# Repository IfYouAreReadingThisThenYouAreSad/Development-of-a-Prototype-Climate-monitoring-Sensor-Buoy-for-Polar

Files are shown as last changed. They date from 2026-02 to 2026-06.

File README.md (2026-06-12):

# Development of a Prototype Climate-Monitoring Sensor Buoy for Polar Regions

---

# 1.0 About

This project aims to develop a prototype of a mass-deployable climate-monitoring buoy optimised for polar regions. The system autonomously measures and communicates key environmental parameters such as sea ice thickness, temperature, salinity, and local imagery. It is intended for deployment in both ice and open water, operating with minimal energy and maintenance.

Project Demo (https://www.youtube.com/watch?v=G8KJ4cSrFfc)

---

# 2.0 Sensors

The buoy contains sensors that help measure essential climate variables and the overall health of the buoy. Sensors include:

- Sea ice thickness (EMI)
- Turbidity
- Salinity (and possible antifouling monitoring)
- UV and ambient light exposure
- Temperature (external)
- Temperature (internal)
- Tilt (compensates for angle for the sea ice measurement system)
- IMU (wave spectrum)
- GPS
- Bluetooth (for the prototype only, will be replaced by satellite communication)
- Battery monitoring
- SD card (onboard storage)
- Camera (with onboard image processing)

The image below shows the buoy's sensors and their locations.

<p align="center">
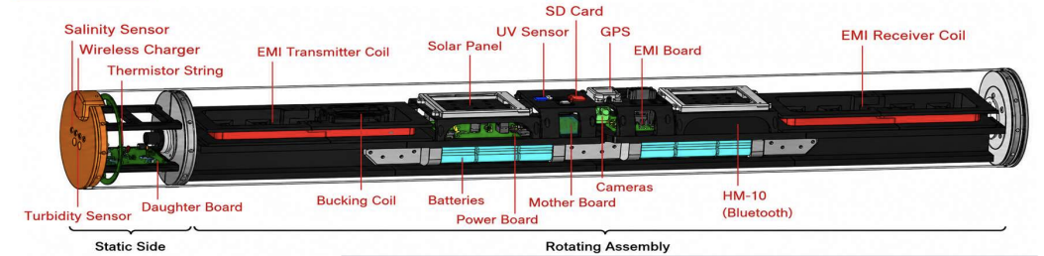
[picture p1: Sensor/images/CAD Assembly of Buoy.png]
Figure 1 shows CAD View of Buoy
  
</p>
<p align="center">Figure 1: CAD view of the buoy</p>

---

# 3.0 Mechanical Design

The buoy has a rotating side and a static side. The static side contains sensors such as turbidity and salinity, the external temperature sensors, and the IMU. These need to stay fixed, and this side is weighted slightly so that, in water, they can work effectively without being affected by the rotating part of the system.

The buoy has a rotating side, where a rotating I-beam is used to ensure proper orientation of the buoy. Due to the buoy being mass-deployed and dropped anywhere in the Arctic, this allows the system to always align orientation-sensitive sensors, such as the EMI sensor, which must always be horizontal to the sea ice. It also keeps the GPS, UV sensor, and Bluetooth module pointing towards the sky, and the camera pointing perpendicular to the ice for the best view.

For both sides to work, two PCBs (shown below) were made, connected through a slip ring. The daughter board digitises the data on the static side and adds a checksum. The mother PCB then reads this data and sends it via satellite. This is a very brief explanation — for more detail, please read the attached report in this repository.

<p align="center">
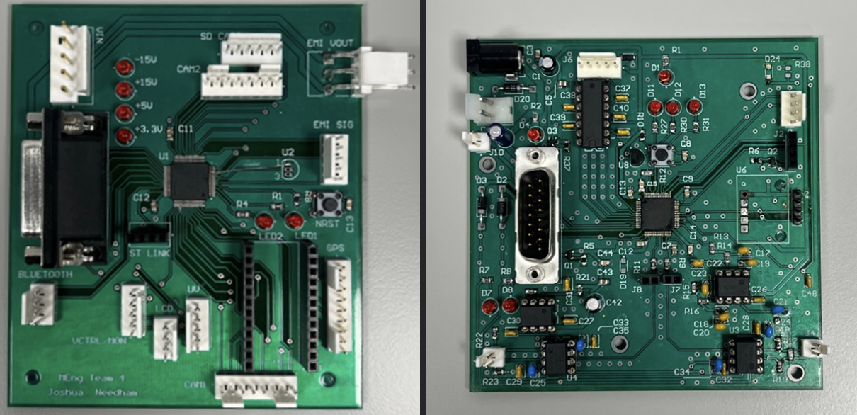
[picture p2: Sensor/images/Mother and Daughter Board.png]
Figure 2 shows the Mother and Daughter board
  
</p>
<p align="center">Figure 2: Mother and daughter boards</p>

---

# 4.0 GUI

A GUI was designed to interact with the system. This allows for monitoring of the buoy and for manual requests of data. In this prototype, data must be requested manually, but in the real system data will be sent periodically, with the frequency changing depending on whether the buoy is on ice, in water, or on land. The GUI in the real design will still allow specific data to be requested, but will also allow monitoring of the health, position, and data of multiple buoys. An image of the GUI is shown below.

<p align="center">
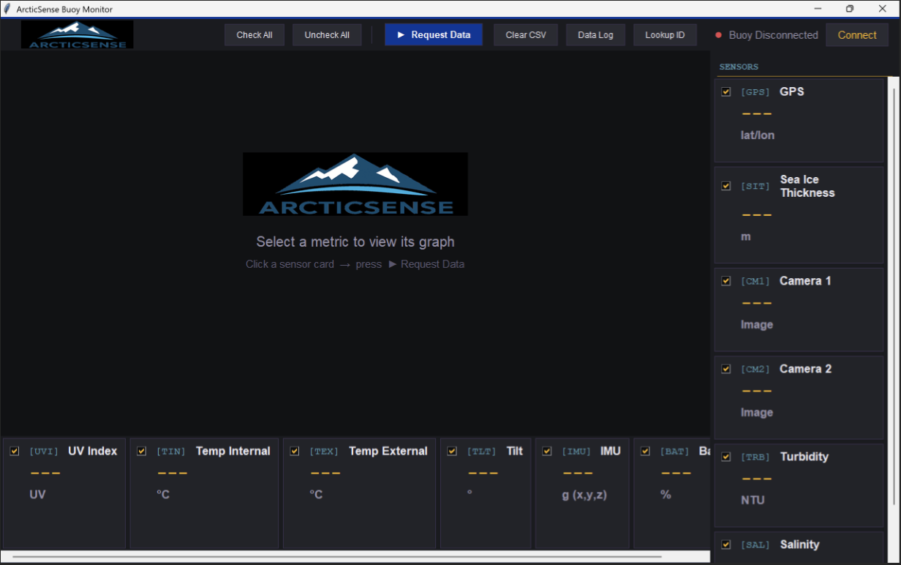
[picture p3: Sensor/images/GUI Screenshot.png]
Figure 3 shows GUI Interface
  
</p>
<p align="center">Figure 3: GUI interface</p>

---

# 5.0 System Architecture

<p align="center">
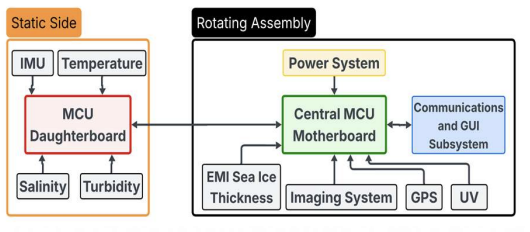
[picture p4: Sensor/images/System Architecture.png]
Figure 4 shows simplified System Architecture of Buoy
  
</p>
<p align="center">Figure 4: Simplified system architecture of the buoy</p>

---

# 6.0 Repository Structure

This repository is organised into folders, each corresponding to a specific sensor, hardware module, or subsystem. Code for each module was developed, compiled, and tested independently within its respective folder. Once verified, each module's code is integrated into a single project that combines all sensors, hardware, and subsystems into a fully functioning system.

This structure is designed to make it easier for external users to:

- Understand how each module works individually
- Navigate to specific hardware or sensor code
- Contribute to or modify individual subsystems without affecting the rest of the project

## Folder Overview

| Folder | Contents |
|--------|----------|
| `README` | This top-level overview of the project. |
| `Intergration` | The integrated mother and daughter board projects (`main.c` for each), the GUI application, and their associated READMEs. |
| `Sensors` | One folder per sensor/module, each containing its driver library and a README explaining its hardware, API, and usage. |
| `Report and Other Information` | The full project report and the project poster. |
| `PCB` | PCB design files for the mother and daughter boards. This may be sent separately if it isn't ready in time for handover. |

---

# 7.0 More Information

Each README in this repository is intentionally short, providing baseline information on the hardware and how to use the code associated with each sensor or section. For more information, calibration data, and results, please read the report attached in this repository.

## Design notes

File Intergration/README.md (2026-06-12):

# ArcticSense

A prototype autonomous climate-monitoring sensor buoy designed for polar deployment. The system collects Essential Climate Variables such as sea ice thickness, ocean temperature, turbidity, salinity, and UV radiation, then transmits them remotely to a ground-station GUI.

Developed as a final-year engineering project in partnership with the **British Antarctic Survey**.

---

## System Overview

```
Ground Station (Python GUI)
        │
        │  Bluetooth Low Energy (HM-10)
        │  [target: Iridium 9603N satellite modem]
        ▼
┌─────────────────────────────────────┐
│        Motherboard  (STM32F405RGT6) │
│  UV · GPS · Tilt · Battery          │
│  EMI · Cameras · Temp · Humidity    │
│                      UART ↕         │
│      Daughterboard  (STM32F405RGT6) │
│  Thermistors · Turbidity · Salinity │
│  Temp · Humidity· IMU               │
└─────────────────────────────────────┘
```

The **Motherboard (MB)** receives commands from the GUI, forwards the request to the **Daughterboard (DB)**, reads its own sensors, assembles the combined payload, and returns it to the GUI as 20-byte fragments. The DB is a silent slave, it never initiates communication.

The **HM-10 BLE module** is a development stand-in for the target **Iridium 9603N** satellite modem. The 20-byte fragment size and 5-byte command frame were chosen to fit within the Iridium SBD 340-byte message limit, so migrating to satellite requires only a transport-layer swap.

---

## Quick Start

To run the ground station on a laptop with BLE:

```bash
cd GUIV3
pip3 install bleak Pillow tkintermapview matplotlib
python3 run.py
```

See [`GUI/README.md`](GUI/README.md) for full setup instructions, file layout, and GUI feature reference.

To flash firmware, open either the `Motherboard/` or `Daughterboard/` project in **STM32CubeIDE** and flash via ST-Link.

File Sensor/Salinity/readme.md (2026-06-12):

# Salinity (STM32)

---

# 1. Overview

A custom made salinity sensor was made for the buoy to save money and to help expand the functionality of traditional salinity sensors. A 4-probe salinity sensor was used, which leads to better long-term measurements than a traditional 2-probe sensor. The sensor calculates salinity through the cell constant, which was found through calibration (read the final report for more information). Additionally, the salinity sensor has also been calibrated for some temperature change, but more work needs to be done on this.

---

# 2. Hardware

The sensor uses the daughter board's DAC. This is run through a low-pass filter, or can be jumped with a 0Ω resistor so it acts as a unity gain amplifier. Next, the signal goes through an AC coupling stage to remove any DC components from the DAC. It is then passed through a shunt resistor before going to the outer electrodes. The voltage across the shunt goes through an instrumentation amplifier, which adds gain and shifts it up to 1.65V to use the ADC's full range. The inner electrodes go through a duplicate instrumentation amplifier arrangement. All of this is shown in the image below.

<p align="center">
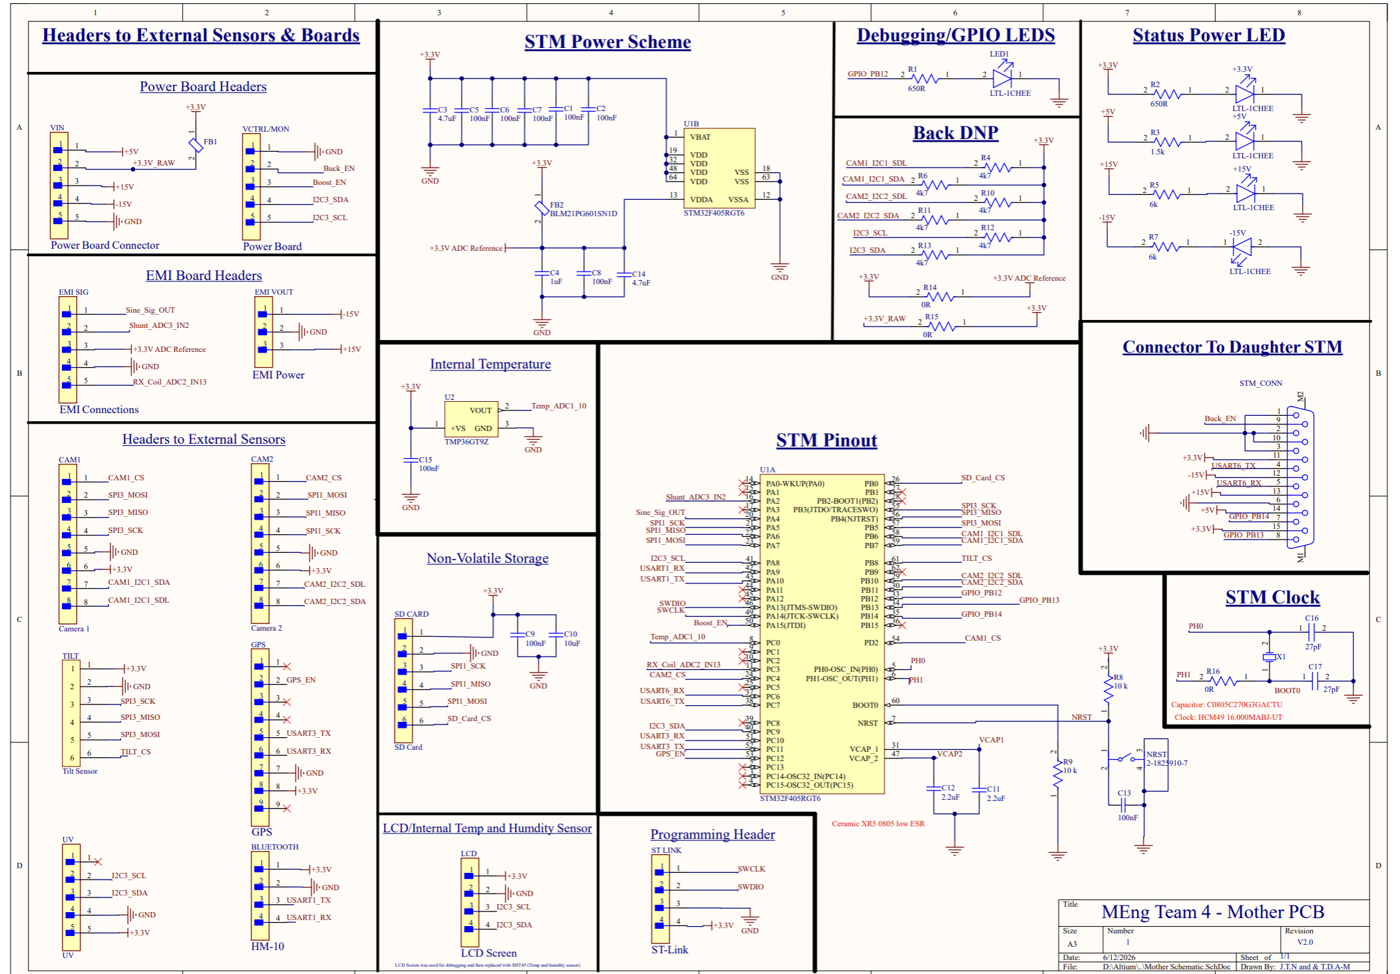
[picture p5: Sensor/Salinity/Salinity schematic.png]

</p>

<p align="center"><b>Figure 1:</b> Salinity sensor signal chain — DAC excitation, AC coupling, shunt, and instrumentation amplifier stages.</p>

---

# 3. Hardware Connections

The salinity sensor is driven and read via the **STM32 DAC and ADC** peripherals, not I2C.

## STM32 ↔ Salinity Circuit Connections

| Signal | STM32 / System | Description                                      |
|--------|-----------------|---------------------------------------------------|
| DAC_OUT2 | DAC Channel 2 | 7 Hz sine excitation signal, sent to outer electrodes via shunt |
| ADC1_IN9 | ADC1 (master) | Current channel (shunt voltage), DMA captured     |
| ADC2_IN14 | ADC2 (slave)  | Voltage channel (inner electrode voltage), DMA captured |
| TIM6    | Timer          | Triggers the DAC sine output (448 Hz update rate, 64-point LUT) |
| TIM3    | Timer          | Triggers simultaneous dual ADC1/ADC2 sampling     |

---

# 4. API

This module is implemented directly in `main.c` rather than as a separate driver library, as only one measurement function is required.

## Public Functions

| Function | Description |
|----------|-------------|
| `ConductivityResult Conductivity_Measure(void)` | Runs a full conductivity/salinity measurement cycle: safety check, DAC excitation, dual-ADC DMA capture, and conversion to conductivity and salinity. Always check `.status` before using the returned values. |

---

## Important `#define` Constants

| Variable | Description |
|----------|-------------|
| `SINE_SAMPLES` | Number of points in the DAC sine LUT (64). |
| `SINE_FREQ_HZ` | Excitation frequency (7 Hz). |
| `DAC_MID_COUNT` / `DAC_AMP_COUNT` | DAC LUT mid-rail and amplitude counts, set for a 1Vpp sine centred at 1.65V on a 3.3V/12-bit DAC. |
| `CYCLES_TO_CAPTURE` | Number of excitation cycles captured per measurement (16). |
| `ADC_BUF_SIZE` | Total dual-word ADC samples captured per measurement (`CYCLES_TO_CAPTURE * SINE_SAMPLES` = 1024). |
| `VREF` / `ADC_FULL_SCALE` | ADC reference voltage (3.3V) and full-scale count (4095) used to convert raw counts to volts. |
| `ADC_SAFETY_THRESHOLD` | Raw ADC count (~3.22V) above which a probe is considered shorted before excitation starts. |
| `CONDUCTIVITY_SCALE` | Cell constant used to convert the current/voltage RMS ratio to conductivity (mS), found through calibration. |
| `SALINITY_SCALE` | Constant used to convert conductivity (mS) to salinity (g/L). |

---

## Enums and Structs

### `ConductivityStatus`

Returned by `Conductivity_Measure()` for error handling.

| Value | Description |
|-------|-------------|
| `COND_OK` | Measurement completed successfully. |
| `COND_FAULT_SHORT` | ADC read close to 3.3V before excitation started, or the voltage channel read near zero — indicates a short or open circuit on the probes. |
| `COND_FAULT_TIMEOUT` | DMA capture did not complete within the 3 second timeout. |

### `ConductivityResult`

Struct returned by `Conductivity_Measure()`.

| Member | Description |
|--------|-------------|
| `ConductivityStatus status` | Result status — must be checked before using the other fields. |
| `float adc1_rms_V` | AC-RMS voltage measured on ADC1 (current/shunt channel). |
| `float adc2_rms_V` | AC-RMS voltage measured on ADC2 (voltage channel). |
| `float conductivity_mS` | Calculated conductivity in mS. |
| `float salinity_gL` | Calculated salinity in g/L. |

---

# 5. Code Flow

## Processing Steps

1. **Safety check**
   - Performs one poll-mode ADC conversion on each channel before any excitation is applied
   - If either ADC reads above `ADC_SAFETY_THRESHOLD` (~3.22V), the probes are assumed shorted and the measurement aborts with `COND_FAULT_SHORT`
   - Re-initialises ADC1 and ADC2 back into their DMA-triggered configuration afterwards

2. **Excitation**
   - Builds a 64-point sine LUT for a 1Vpp, 1.65V-centred signal
   - Starts the DAC on Channel 2 via DMA, driven by TIM6 to produce a 7 Hz sine wave
   - Waits ~50 ms (half a cycle) for the signal to settle

3. **Capture**
   - Starts simultaneous dual-ADC DMA capture (ADC1 master / ADC2 slave), triggered by TIM3
   - Captures 1024 dual-word samples (16 full excitation cycles)
   - Waits for DMA completion, with a 3 second timeout (`COND_FAULT_TIMEOUT` if exceeded)

4. **Shutdown**
   - Stops TIM3, ADC DMA, TIM6, and the DAC in sequence
   - Parks the DAC output at mid-rail (1.65V) briefly before stopping it, to avoid a floating-output glitch

5. **Conversion**
   - Computes the AC-RMS voltage of each channel (DC bias removed via a two-pass mean/variance calculation)
   - If the voltage channel RMS is near zero, returns `COND_FAULT_SHORT` (likely open circuit)
   - Calculates conductivity: `conductivity_mS = (I_rms / V_rms) * CONDUCTIVITY_SCALE`
   - Calculates salinity: `salinity_gL = conductivity_mS * SALINITY_SCALE`

---

# 6. Dependencies

- STM32 HAL Library
- STM32 ADC1 and ADC2 Peripherals (dual-simultaneous DMA mode)
- STM32 DAC Peripheral (Channel 2, DMA mode)
- TIM6 (DAC trigger) and TIM3 (ADC trigger)
- `math.h` (for sine LUT generation)

---

# 7. Example Usage (C)

```c
ConductivityResult result = Conductivity_Measure();

if (result.status == COND_OK)
{
    float conductivity = result.conductivity_mS;
    float salinity     = result.salinity_gL;

    BSP_LED_Toggle(LED_GREEN);
}
else if (result.status == COND_FAULT_SHORT)
{
    // Probe short or open circuit detected
    Error_Handler();
}
else
{
    // ADC DMA timeout — check TIM3 and DMA configuration
    Error_Handler();
}
```

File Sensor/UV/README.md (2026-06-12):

# UV Module (STM32)

If you are looking for libraries for **Arduino or Raspberry Pi** and information on the **LTR390-UV Ultraviolet Sensor**, please refer to the official Waveshare Wiki documentation:

https://www.waveshare.com/wiki/UV_Sensor_(C)

---

# 1. Overview

This directory contains a driver for interfacing with the **Digital LTR390-UV Ultraviolet Sensor** over I2C using an STM32 microcontroller.

The LTR390 enables real-time measurement of:
- Ambient light using the onboard ambient light sensor (ALS)
- Ultraviolet light

This module is used on the buoy to monitor UV light across seasons to help monitor climate change.

---

# 2. Hardware

The system uses the:

**Digital LTR390-UV Ultraviolet Sensor**

### Product Link
https://thepihut.com/products/digital-ltr390-uv-ultraviolet-sensor

<p align="center">
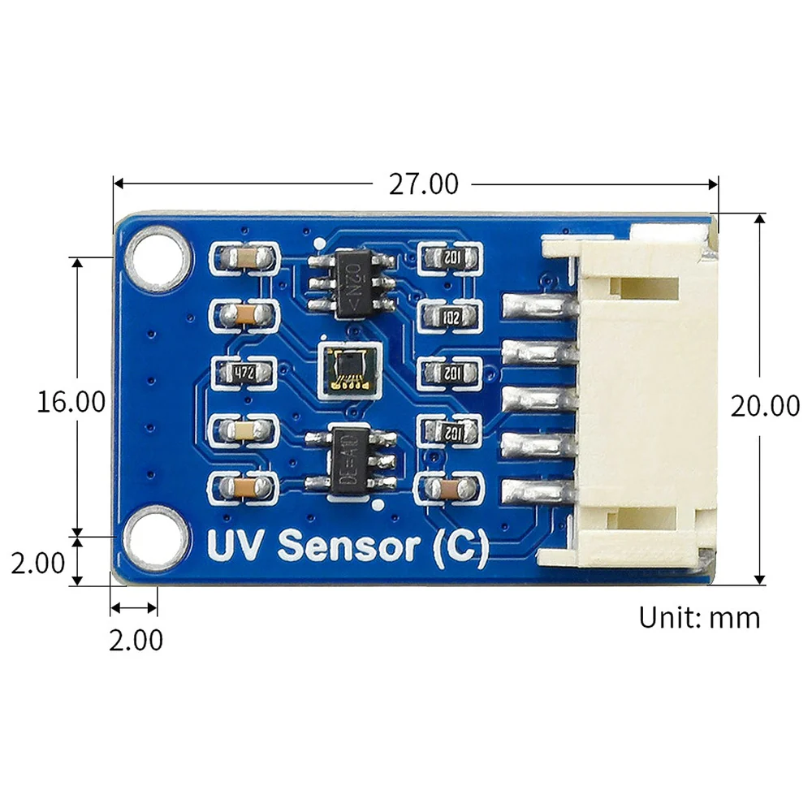
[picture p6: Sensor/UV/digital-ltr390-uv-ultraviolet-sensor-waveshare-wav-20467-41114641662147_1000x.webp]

</p>

<p align="center"><b>Figure 1:</b> UV Sensor Module</p>

---

# 3. Hardware Connections

The LTR390 communicates via the **I2C interface**.

## STM32 ↔ LTR390 Connections

| LTR390 Pin | STM32 / System | Description       |
|------------|----------------|-------------------|
| VCC        | 3.3V / 5V      | Module power      |
| GND        | GND            | Common ground     |
| SCL        | I2C_SCL        | I2C clock line    |
| SDA        | I2C_SDA        | I2C data line     |

---

## Example STM32F401 Pin Mapping

| STM32 Pin | Peripheral | Function  |
|-----------|------------|-----------|
| PB6       | I2C1_SCL   | I2C clock |
| PB7       | I2C1_SDA   | I2C data  |

---

# 4. API

## Constructor

| Function | Description |
|----------|-------------|
| `Ltr390Driver(I2C_HandleTypeDef *hi2c_)` | Initialises the driver with the STM32 I2C peripheral. Internal variables are reset during construction. |

---

## Important `constexpr` Class Variables

These variables are held constant at compile time and are currently set for this project's application. It may be worth reviewing these before compiling for a different project.

These constants are private members of the class in the `.hpp` file and are intentionally hidden from the user to prevent accidental modification.

| Variable | Description |
|----------|-------------|
| `WINDOW_FACTOR` | Compensates for UV loss through the buoy enclosure window. Set to 1.0 until the window material has been calibrated. |
| `DATA_READY_TIMEOUT_MS` | Maximum time the driver waits for the sensor to be ready before returning a `TIMEOUT` error. Used in `wait_data_ready()`. |
| `MEAS_RATE_DEFAULT` | Controls resolution and measurement rate. Bits [6:4] set resolution, bits [2:0] set rate. `ALS_INTEGRATION_TIME` updates automatically when this changes. |
| `GAIN` | Sets the photodiode gain. `ALS_GAIN` updates automatically when this changes. |
| `COUNTS_PER_UVI` | Reference sensitivity constant used to convert raw UV counts to UV Index. Must be recalculated from the datasheet if `GAIN` or `MEAS_RATE_DEFAULT` are changed. |

---

## Public Functions

| Function | Description |
|----------|-------------|
| `Ltr390Status init()` | Initialises the sensor by probing the I2C bus, setting resolution, sampling rate, and gain, then enabling the sensor in UV mode. |
| `Ltr390Status calculate_uv_index()` | Reads the UV sensor and calculates the UV Index. Result is stored internally and retrieved with `get_uv_index()`. |
| `Ltr390Status calculate_lux()` | Reads the ambient light sensor and calculates lux. Result is stored internally and retrieved with `get_lux()`. |
| `float get_uv_index()` | Returns the last UV Index value computed by `calculate_uv_index()`. |
| `float get_lux()` | Returns the last lux value computed by `calculate_lux()`. |

---

# 5. Enums

## `Ltr390Status`

Returned by all driver functions for error handling and debugging.

| Value | Description |
|-------|-------------|
| `Ltr390Status::OK` | Operation successful. |
| `Ltr390Status::I2C_NO_ACKNOWLEDGMENT` | Sensor did not ACK — check wiring, power, and I2C address. |
| `Ltr390Status::I2C_TRANSMIT_ERROR` | I2C failure when transmitting to the sensor. |
| `Ltr390Status::I2C_RECEIVE_ERROR` | I2C failure when receiving data from the sensor. |
| `Ltr390Status::TIMEOUT` | Sensor did not signal data ready within `DATA_READY_TIMEOUT_MS`. |
| `Ltr390Status::INVALID_ARGUMENT` | Invalid `WINDOW_FACTOR` value (must be greater than 0). |
| `Ltr390Status::RESOLUTION_SETUP_ERROR` | I2C error when writing the resolution / measurement rate register. |
| `Ltr390Status::GAIN_SETUP_ERROR` | I2C error when writing the gain register. |
| `Ltr390Status::UV_MODE_SWITCH_ERROR` | Failed to switch the sensor to UV measurement mode. |
| `Ltr390Status::ALS_MODE_SWITCH_ERROR` | Failed to switch the sensor to ambient light measurement mode. |

---

# 6. Code Flow

<p align="center">
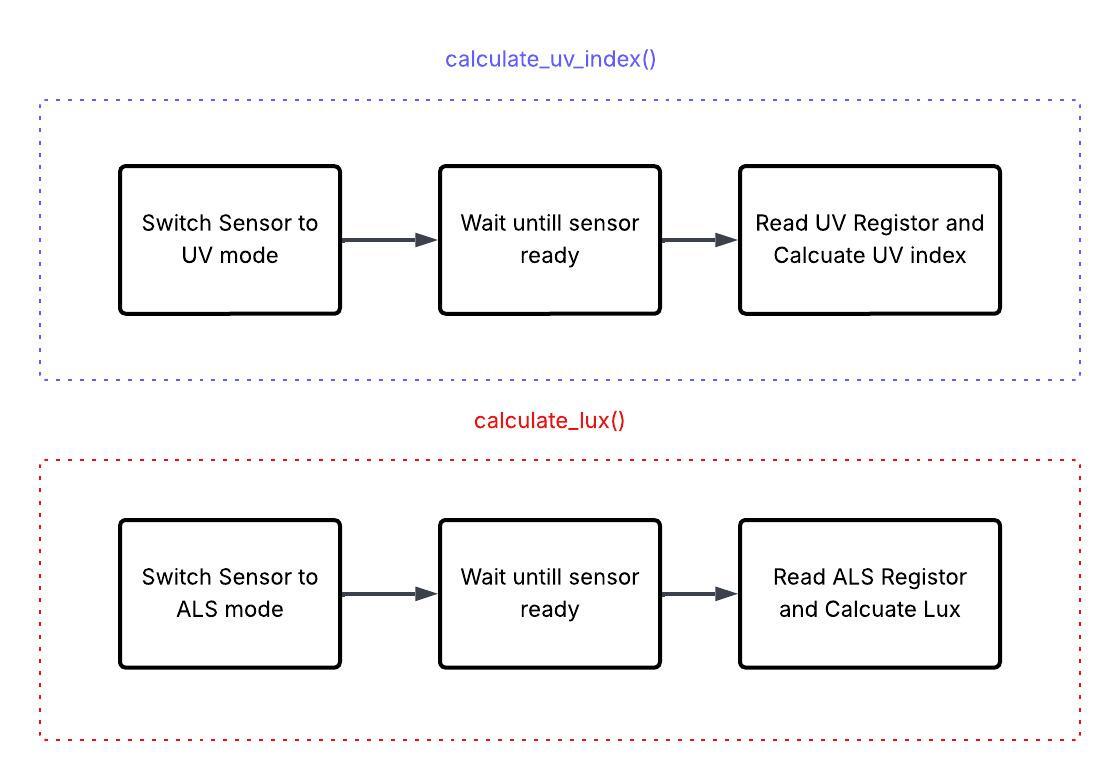
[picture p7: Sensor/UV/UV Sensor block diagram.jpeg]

</p>

<p align="center"><b>Figure 2:</b> LTR390 Processing Pipeline for Calculating UV Index and Lux</p>

## Processing Steps

1. **Initialisation (run once)**
   - Probes the I2C bus to confirm the sensor is present
   - Sets resolution and sampling rate
   - Sets gain
   - Enables the sensor in UV mode

2. **UV Measurement**
   - Switches sensor to UV mode
   - Waits until the sensor signals data is ready
   - Reads raw 24-bit UV count
   - Calculates UV Index: `UVI = (counts / COUNTS_PER_UVI) * WINDOW_FACTOR`

3. **Lux Measurement**
   - Switches sensor to ALS mode
   - Waits until the sensor signals data is ready
   - Reads raw 24-bit ALS count
   - Calculates lux: `Lux = (0.6 * counts) / (gain * integration_time)`

---

# 7. Dependencies

- STM32 HAL Library
- STM32 I2C Peripheral

The correct HAL header is selected automatically at compile time based on the target STM32 family defined in your build flags (e.g. `-DSTM32F401xE`). Supported families are listed in `ltr390_driver.hpp`.

---

# 8. Example Usage (C++)

```cpp
Ltr390Driver ltr390_sensor(&hi2c1);

float debug_uv_index = 0.0f;
float debug_lux      = 0.0f;

Ltr390Status init_status = ltr390_sensor.init();
if (init_status != Ltr390Status::OK) {
    Error_Handler();
}

while (1)
{
    (void)ltr390_sensor.calculate_uv_index();
    (void)ltr390_sensor.calculate_lux();

    debug_uv_index = ltr390_sensor.get_uv_index();
    debug_lux      = ltr390_sensor.get_lux();

    BSP_LED_Toggle(LED_GREEN);
    HAL_Delay(500);
}
```

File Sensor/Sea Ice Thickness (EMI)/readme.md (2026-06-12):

# Sea Ice Thickness Sensor using EMI (STM32)

---

# 1. Overview

The USP of the buoy was that it can measure sea ice non-destructively, which no other buoy on the market does to date. An electromagnetic sensing system was custom made in order to do this, shown below in a testing photo. This works by driving a transmitter coil using a power amplifier with a high frequency changing voltage, which creates a magnetic field that then produces eddy currents in the sea water. These eddy currents create a magnetic field that opposes the magnetic field of the transmitter coil (Lenz's law). This secondary changing field is then picked up by the receiver coil, which allows us to infer sea ice thickness from the magnitude and in-phase response, as shown in Figure 2 below. (Note: a bucking coil of 1 turn was added to the system to stop any primary coupling between the transmitter (Tx) coil and receiver (Rx) coil, which is not shown on the explanation diagram below.)

<p align="center">
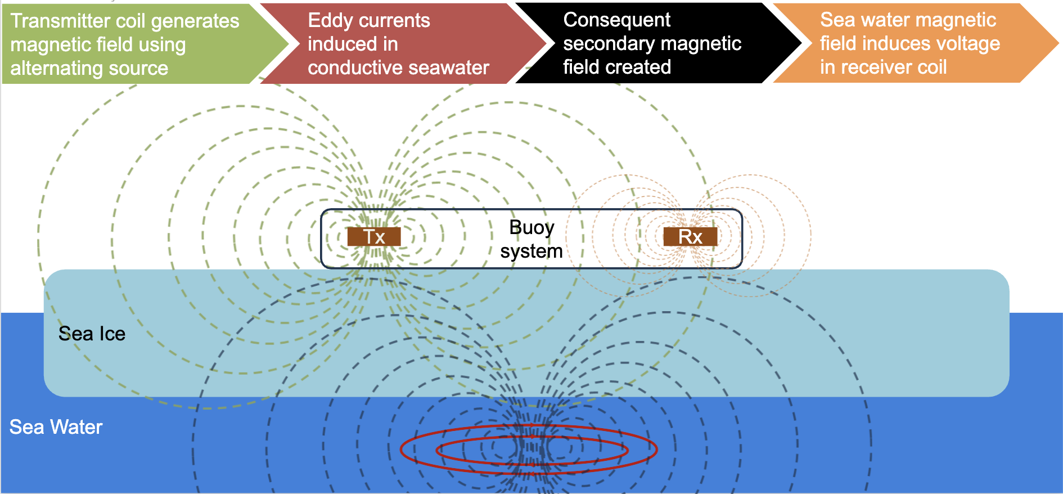
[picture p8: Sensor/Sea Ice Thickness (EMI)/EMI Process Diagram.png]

</p>

<p align="center"><b>Figure 1:</b> EMI interaction with seawater.</p>

<p align="center">
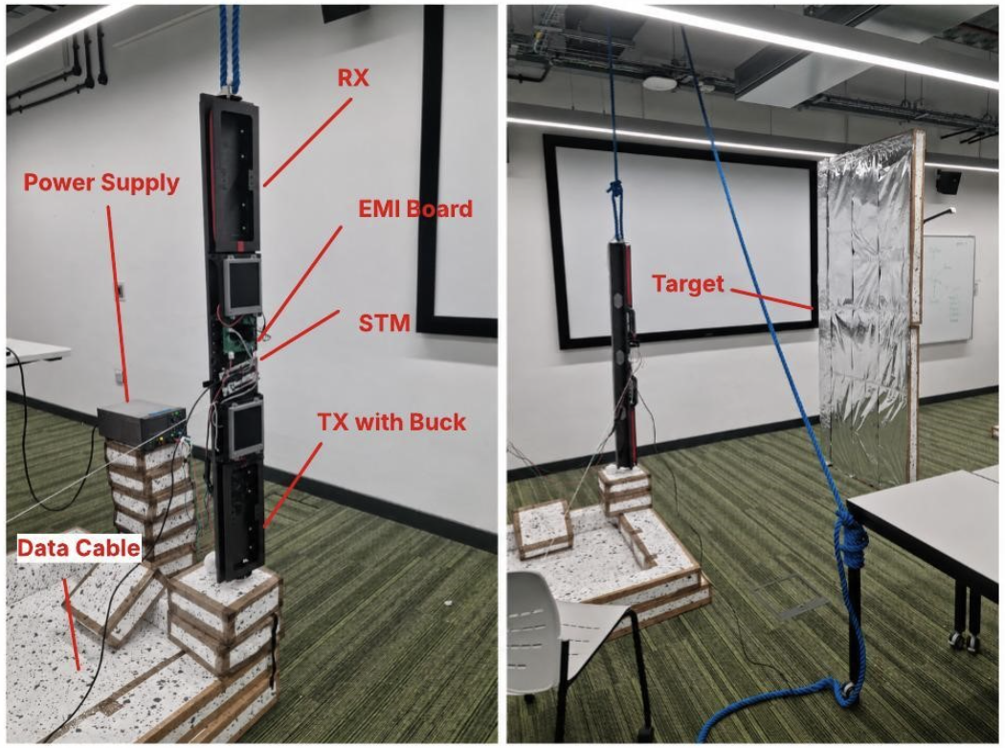
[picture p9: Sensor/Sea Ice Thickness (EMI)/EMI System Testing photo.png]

</p>

<p align="center"><b>Figure 2:</b> EMI system photo.</p>

A custom EMI board was made for this, where a DAC signal and +15V/-15V rails are fed into the PCB. The DAC on the STM32F405RGT6 produces a 20 kHz, 1.2 V peak-to-peak signal, which is passed into the EMI PCB and then amplified up using a power amplifier and sent to the Tx coil, where the current is measured by a 1Ω shunt, as shown in Figure 3. The Rx coil is fed into the PCB, where parallel resistors and capacitors were added to help increase the sensitivity of the system. The bucking coil was also fed into the Rx header, going to the -Vin of the instrumentation amplifier to subtract the primary field coupling, as shown in Figure 4. Additionally, a 1.65V reference was created using the STM32F405RGT6's 3.3V ADC reference, through a potential divider and unity gain op-amp, to create a low impedance 1.65V reference and utilise the full range of the system's ADC, as shown in Figure 5.

<p align="center">
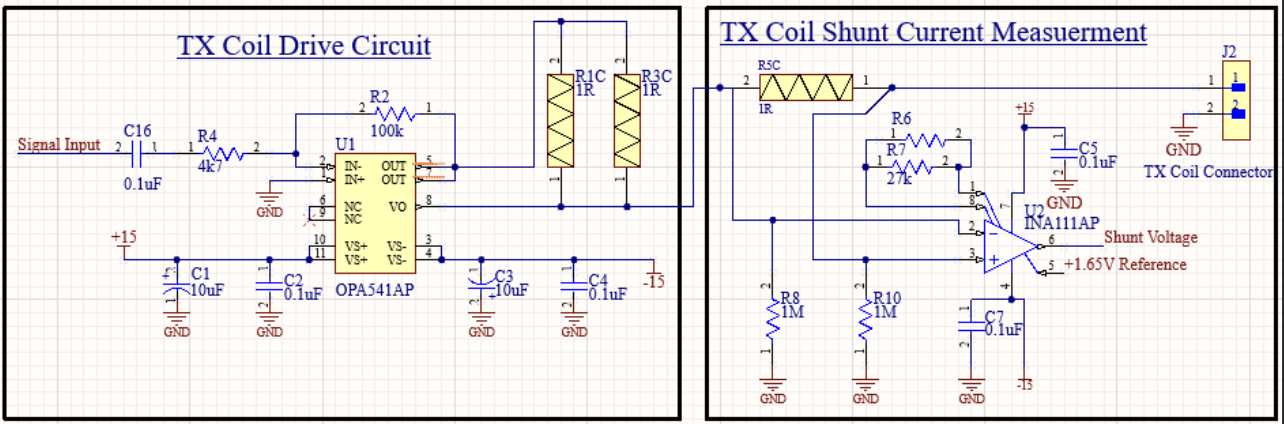
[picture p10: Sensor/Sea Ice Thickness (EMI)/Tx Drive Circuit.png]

</p>

<p align="center"><b>Figure 3:</b> Power Amplifier (Tx Drive) and Shunt Circuit.</p>

<p align="center">
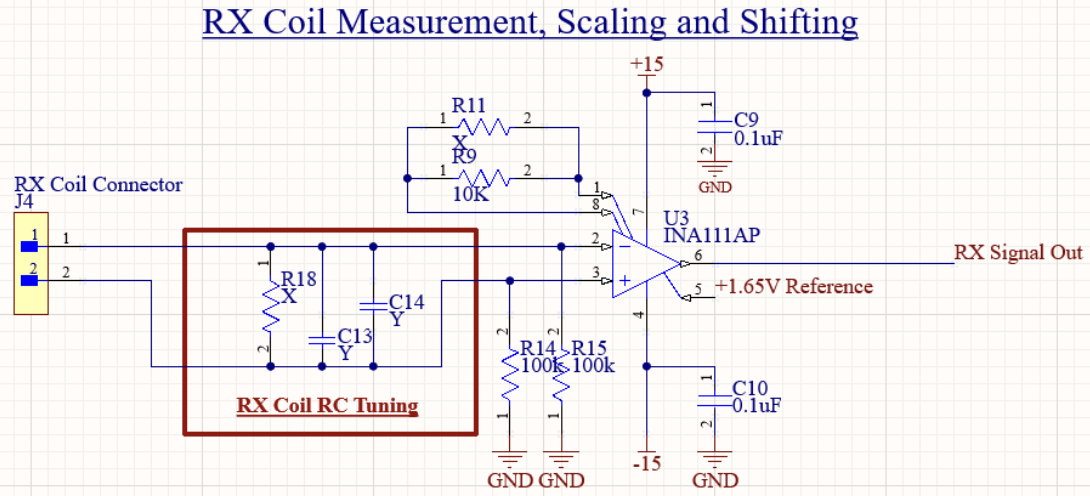
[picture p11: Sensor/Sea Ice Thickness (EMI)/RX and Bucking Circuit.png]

</p>

<p align="center"><b>Figure 4:</b> Rx Resonating and Bucking Subtraction Circuit.</p>

<p align="center">
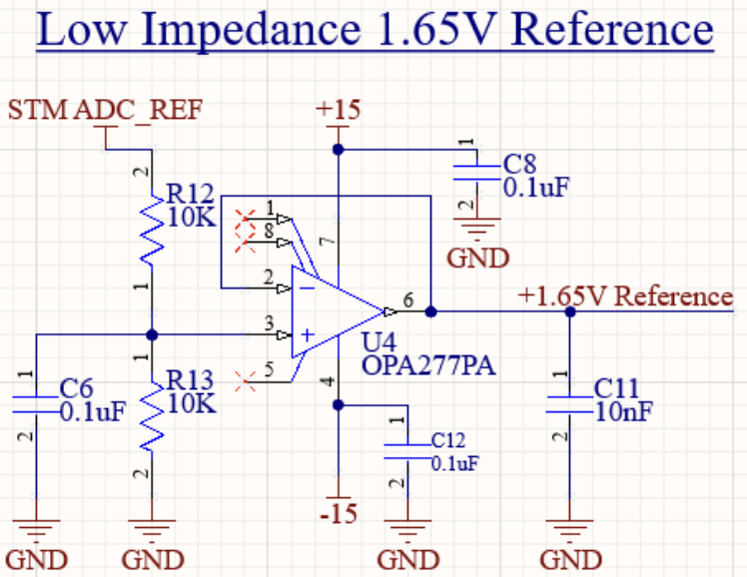
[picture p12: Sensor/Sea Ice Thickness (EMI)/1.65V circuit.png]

</p>

<p align="center"><b>Figure 5:</b> 1.65V Reference Circuit.</p>

---

# 2. Hardware

The system uses the:

**OPA541AP Texas Instruments, Operational Amplifier, 2 MHz, 11-Pin 40V TO-220 (Power Amplifier)**

### Product Link
https://uk.rs-online.com/web/p/op-amps/1977445?gb=a

### Datasheet
https://www.ti.com/lit/ds/symlink/opa541.pdf?ts=1781225701324

**INA111AP Texas Instruments Instrumentation Amplifier, ±1000 μV Offset 2 MHz, 8-Pin 4.5 mA PDIP (Instrumentation Amplifier)**

### Product Link
https://uk.rs-online.com/web/p/instrumentation-amplifiers/1977135?gb=a

### Datasheet
https://www.ti.com/lit/ds/symlink/ina111.pdf?ts=1781246890532&ref_url=https%253A%252F%252Fwww.google.com%252F

**OPA277PA Texas Instruments, Operational Amplifier, 1 MHz, 8-Pin 18V PDIP (Op-Amp)**

### Product Link
https://uk.rs-online.com/web/p/op-amps/3071667

### Datasheet
https://www.ti.com/lit/ds/sbos079c/sbos079c.pdf?ts=1781237728977

---

# 3. CubeMX Settings

Note: to produce a 20 kHz signal with the DAC, the clock settings and prescaler will have to be changed, with the addition of using a timer in order to trigger the DAC. For the ADCs to record the shunt and Rx voltage, a rank was used with DMA for both ADCs and the DAC. DMA must be used, especially for the DAC, to generate the 20 kHz, 1-1.2 V peak-to-peak sine wave, or it will be distorted or at the wrong frequency.

---

# 4. Hardware Connections

The EMI sensor is read via the **STM32 DAC and ADC** peripherals, clocked in lock-step by a timer.

## STM32 ↔ EMI PCB Connections

| STM32 Pin | Peripheral | Description                              |
|-----------|------------|-------------------------------------------|
| PA4       | DAC_OUT1   | 20 kHz sine drive signal to Tx power amp   |
| PC3       | ADC2_IN13  | Rx coil / shunt output, lock-in capture    |
| TIM6      | Timer      | Clocks both DAC DMA and ADC2 DMA in lock-step |

**Bit-conflict note:** EMI is registered at bit 6 in the sensor registry. The UV/lux sensor was also at bit 6 — it must be moved to bit 5 (or any other free bit) in `sensor_registry.cpp`.

---

# 5. API

## Initialisation

| Function | Description |
|----------|-------------|
| `void emi_init(void)` | Builds the DAC sine LUT and the reference I/Q LUTs. Called once from `sensors_init()`. |

---

## Public Functions

| Function | Description |
|----------|-------------|
| `void emi_init(void)` | Builds the DAC sine LUT and reference I/Q LUTs used for the lock-in calculation. |
| `void emi_read(uint8_t *out)` | Runs `EMI_NUM_REPS` timer-triggered DMA captures, averages the corrected lock-in results, and writes 20 bytes to `out`. Blocking — returns after all repetitions complete. At default parameters (50 reps, 150 cycles, 128-point LUT, ~2.1 MHz sample rate) this takes approximately 460 ms. |

---

# 6. Output Payload

`emi_read()` writes 20 bytes — five IEEE-754 `float32` values, in order:

| Bytes   | Value | Description |
|---------|-------|-------------|
| 0–3     | `avg_corr_i` | Average corrected in-phase (I) component |
| 4–7     | `avg_corr_q` | Average corrected quadrature (Q) component |
| 8–11    | `avg_corr_mag` | Average corrected magnitude |
| 12–15   | `avg_corr_phase_deg` | Average corrected phase, in degrees (circular mean) |
| 16–19   | `avg_corr_phase_from_iq` | Average phase derived from I/Q, in degrees |

These match the printf order in `print_average_results()` from the EMITesting reference project.

---

# 7. Code Flow

## Processing Steps

1. **Initialisation (run once)**
   - Builds the DAC sine LUT used to drive the Tx coil
   - Builds the reference I/Q LUTs used for the lock-in calculation

2. **Measurement (per `emi_read()` call)**
   - TIM6 triggers DMA-driven output of the sine LUT to the DAC (PA4 → Tx power amp)
   - TIM6 simultaneously triggers DMA-driven ADC2 capture of the Rx/shunt signal (PC3)
   - `EMI_NUM_REPS` capture cycles are performed (default 50 reps × 150 cycles, 128-point LUT, ~2.1 MHz sample rate)

3. **Lock-in Processing & Output**
   - Each capture is correlated against the reference I/Q LUTs to extract the in-phase (I) and quadrature (Q) components
   - I, Q, magnitude, and phase are corrected and averaged across all repetitions (phase using a circular mean)
   - Writes the five resulting `float32` values (I, Q, magnitude, phase, phase-from-I/Q) into the 20-byte output buffer

---

# 8. Dependencies

- STM32 HAL Library
- STM32 DAC Peripheral (DAC_CHANNEL_1)
- STM32 ADC2 Peripheral
- TIM6
- DMA (required for both DAC and ADC2)

See `IOC_SETUP.md` (or the comment block in `emi.c`) for the full `.ioc` configuration prerequisites.

---

# 9. Example Usage (C)

```c
uint8_t emi_buf[20];

emi_init();   // called once from sensors_init()

while (1)
{
    emi_read(emi_buf);   // blocking, ~460 ms at default parameters

    float avg_corr_i, avg_corr_q, avg_corr_mag;
    float avg_corr_phase_deg, avg_corr_phase_from_iq;

    memcpy(&avg_corr_i,             &emi_buf[0],  4);
    memcpy(&avg_corr_q,             &emi_buf[4],  4);
    memcpy(&avg_corr_mag,           &emi_buf[8],  4);
    memcpy(&avg_corr_phase_deg,     &emi_buf[12], 4);
    memcpy(&avg_corr_phase_from_iq, &emi_buf[16], 4);

    BSP_LED_Toggle(LED_GREEN);
    HAL_Delay(500);
}
```

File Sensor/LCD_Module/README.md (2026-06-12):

# LCD Module Driver (STM32)

This library is based heavily on the **Waveshare Arduino LCD library**, but includes several modifications to make it more user-friendly and easier to integrate with STM32 projects.

If you are looking for libraries for **Arduino, ESP32, or Raspberry Pi**, please refer to the official Waveshare documentation:

https://www.waveshare.com/wiki/LCD1602_I2C_Module_(Blue)#C

This LCD module supports **two lines of text** and multiple **font configurations**.
This library uses the **5x8 dot font configuration by default**.

To change the font configuration, edit the `function_set` macro bitmask inside the `.c` or `.cpp` source file.

Relevant documentation for the LCD controller and bitmask configuration can be found below:

* https://files.waveshare.com/wiki/LCD1602-I2C-Module/LCD1602_I2C_Module.pdf
* https://files.waveshare.com/wiki/LCD1602-I2C-Module/AIP31068L.pdf

---

# 1. About

This directory contains the driver used to interface with the **Waveshare LCD1602 I2C Module V2.0** for the buoy project.

The LCD module allows verification of each subsystem during **system startup**. This enables immediate identification of faults, which is especially important when deploying the prototype in remote environments.

Additionally, the LCD is used for **debugging**, which is essential during subsystem integration—particularly for components that cannot easily be stepped through using the **STM32CubeIDE debugger**, such as the camera capture subsystem.

---

# 2. Part Information

The LCD module used is the **Waveshare Blue 16x2 I2C LCD Module (3.3V/5V) with Backlight Controller**.

The display is available with multiple backlight colours including **blue, green, and grey**.

### Product Links

* Waveshare Blue 16x2 I2C LCD Module
  https://thepihut.com/products/waveshare-blue-16x2-i2c-lcd-module-3-3v-5v-with-backlight-control

* Waveshare Green 16x2 I2C LCD Module
  https://thepihut.com/products/waveshare-green-16x2-i2c-lcd-module-3-3v-5v-with-backlight-control

* Waveshare Grey 16x2 I2C LCD Module
  https://thepihut.com/products/waveshare-grey-16x2-i2c-lcd-module-3-3v-5v-with-backlight-control

<p align="center">
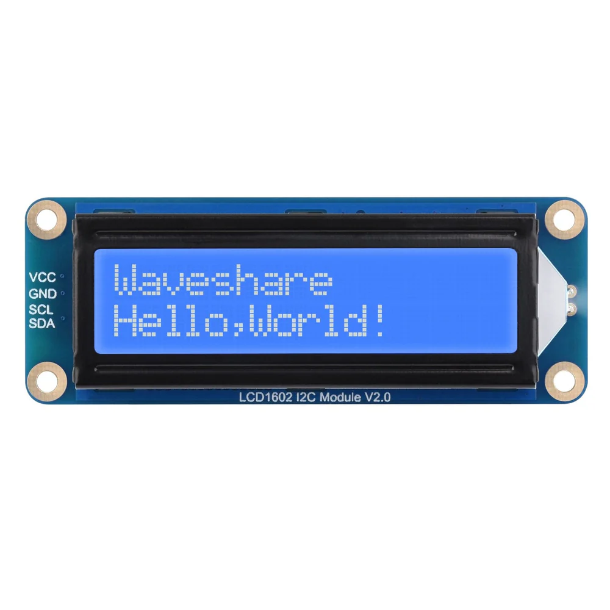
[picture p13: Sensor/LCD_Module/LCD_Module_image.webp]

</p>

<p align="center"><b>Figure 1:</b> Waveshare LCD Module</p>

---

# 3. Tested Hardware

This driver has been tested with:

* **STM32F401RCT6**
* **Waveshare LCD1602 I2C Module V2.0**

---

# 4. Development Environment

| Tool             | Version             |
| ---------------- | ------------------- |
| IDE              | STM32CubeIDE        |
| Version          | 2.0.0               |
| Build            | 26820_20251114_1348 |
| Vendor           | STMicroelectronics  |
| MCU              | STM32F401RCT6       |
| Firmware Library | STM32 HAL           |

---

# 5. Hardware Connections

The LCD module communicates with the STM32 using an **I2C interface**.

## STM32 ↔ LCD Connections

| LCD Pin | STM32 Peripheral | Description   |
| ------- | ---------------- | ------------- |
| VCC     | 3.3V / 5V        | Power supply  |
| GND     | GND              | Ground        |
| SCL     | I2C_SCL          | I2C clock     |
| SDA     | I2C_SDA          | I2C data line |

---

## Example STM32F401 Pin Mapping

| STM32 Pin | Peripheral | Function  |
| --------- | ---------- | --------- |
| PB6       | I2C1_SCL   | I2C clock |
| PB7       | I2C1_SDA   | I2C data  |

---

# 6. API

## Functions

> Note: The C++ implementation uses the same functions as the C API.
> The only difference is that `lcd_startup(..)` is handled automatically by the **class constructor**.

| Function                                             | Description                                                  |
| ---------------------------------------------------- | ------------------------------------------------------------ |
| `lcd_startup(I2C_HandleTypeDef *i2c_pin_assignment)` | Configures the LCD and backlight, and stores the I2C handle. |
| `set_brightness(uint8_t value)`                      | Sets backlight brightness (0–100%).                          |
| `set_led_mode(uint8_t mode)`                         | Sets LED mode: steady (`0x00`) or breathing (`0x20`).        |
| `display_on(void)`                                   | Turns the LCD display on.                                    |
| `display_off(void)`                                  | Turns the LCD display off.                                   |
| `clear(void)`                                        | Clears the display and resets the cursor.                    |
| `set_cursor(uint8_t col, uint8_t row)`               | Moves the cursor to a specific column and row.               |
| `data(uint8_t value)`                                | Sends a single character to the display.                     |
| `send_string(const char *str)`                       | Sends a string to the display.                               |
| `no_cursor(void)`                                    | Hides the cursor.                                            |
| `cursor(void)`                                       | Shows the cursor.                                            |
| `scroll_display_left(void)`                          | Scrolls display left.                                        |
| `scroll_display_right(void)`                         | Scrolls display right.                                       |
| `left_to_right(void)`                                | Sets text direction left-to-right.                           |
| `right_to_left(void)`                                | Sets text direction right-to-left.                           |
| `no_autoscroll(void)`                                | Disables automatic scrolling.                                |
| `autoscroll(void)`                                   | Enables automatic scrolling.                                 |
| `create_char(uint8_t location, uint8_t charmap[])`   | Creates a custom character (CGRAM location 0–7).             |

---

# 7. Enums

## `LCD_STATUS`

This enum is used for **error handling and debugging**.

| Value                              | Description                                                  |
| ---------------------------------- | ------------------------------------------------------------ |
| `LCD_OK`                           | Operation successful                                         |
| `LCD_ERROR_I2C`                    | I2C communication failure when sending data or commands      |
| `LCD_ERROR_I2C_REG`                | I2C communication failure during backlight configuration     |
| `LCD_ERROR_FUNCTION_SET`           | Failed to configure LCD function settings (font, mode, etc.) |
| `LCD_ERROR_DISPLAY_ON`             | Failed to enable the LCD display                             |
| `LCD_ERROR_CLEAR_SCREEN`           | Failed to clear the display                                  |
| `LCD_ERROR_ENTRY_MODE`             | Failed to configure cursor entry mode                        |
| `LCD_ERROR_SETTING_BRIGHTNESS`     | Invalid brightness value passed to `set_brightness(..)`      |
| `LCD_ERROR_SETTING_BACKLIGHT_MODE` | Invalid mode passed to backlight mode function               |
| `LCD_ERROR_SENDING_STRING`         | Failed to send a string to the display                       |
| `LCD_ERROR_CREATE_CHAR`            | Failed to upload custom character data                       |
| `LCD_ERROR_BACKLIGHT_INIT`         | Backlight initialization failed (constructor check)          |
| `LCD_ERROR_LCD_INIT`               | LCD initialization failed (constructor check)                |

---

# 13. Code Flow

<p align="center">
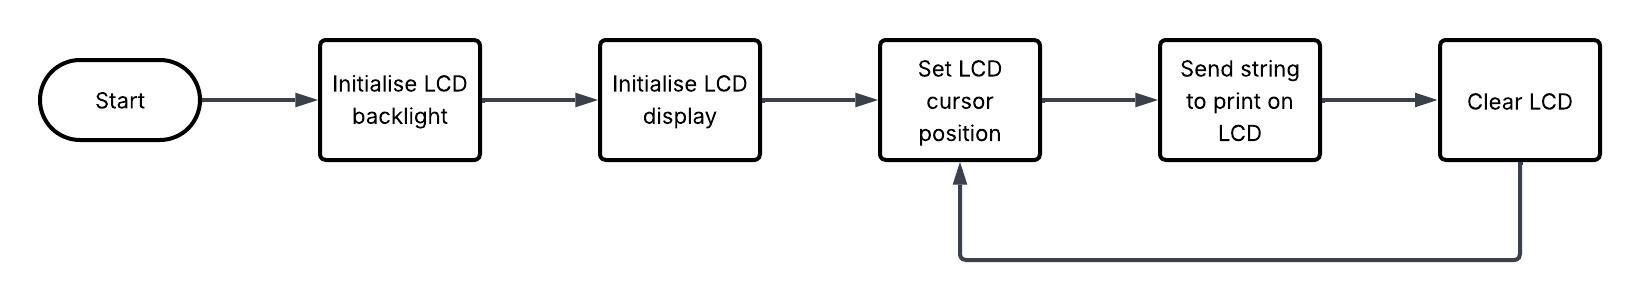
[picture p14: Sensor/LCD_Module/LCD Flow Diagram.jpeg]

</p>

<p align="center"><b>Figure 2:</b> LCD Processing Pipeline</p>

### Processing Pipeline

This is the typical process used when writing text to the display.

1. Configure the LCD backlight controller via **I2C**
2. Configure the LCD controller via **I2C**
3. Set the cursor position via **I2C**
4. Send the string to the LCD via **I2C**
5. Clear the display when needed

For advanced features such as **scrolling animations or custom characters**, see the examples.

---

# 14. Dependencies

* **STM32 HAL Library**
* **STM32 I2C Peripheral**

---

# 15. Example Usage (C)

```c
lcd_startup(&hi2c1);

// Set cursor to first row
set_cursor(0, 0);
send_string("Waveshare");

// Set cursor to second row
set_cursor(0, 1);
send_string("Hello, World!");
```

---

# 16. Example Usage (C++)

```cpp
WaveShareLCD lcd(&hi2c1);

lcd.set_brightness(50);

// First row
lcd.set_cursor(0,0);
lcd.send_string("Waveshare");

// Second row
lcd.set_cursor(0,1);
lcd.send_string("Hello, World!");
```

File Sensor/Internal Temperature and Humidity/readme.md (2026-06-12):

# Internal Temperature and Humidity Module (STM32)

If you are looking for libraries for **Arduino or Python** and information on the **SHT45 Temperature & Humidity Sensor**, please refer to the official Adafruit documentation:

https://learn.adafruit.com/adafruit-sht40-temperature-humidity-sensor/overview

---

# 1. Overview

This directory contains a driver for interfacing with the **Adafruit Sensirion SHT45 Precision Temperature & Humidity Sensor - STEMMA QT / Qwiic** over I2C using an STM32 microcontroller.

The SHT45 enables real-time measurement of:
- Temperature
- Humidity

This module is used on the buoy to monitor internal temperature inside the buoy and humidity inside the buoy for long term health monitoring and camera decisions.

---

# 2. Hardware

The system uses the:

**SHT45 Precision Temperature & Humidity Sensor**

### Product Link
https://thepihut.com/products/adafruit-sensirion-sht45-precision-temperature-humidity-sensor-stemma-qt-qwiic

<p align="center">
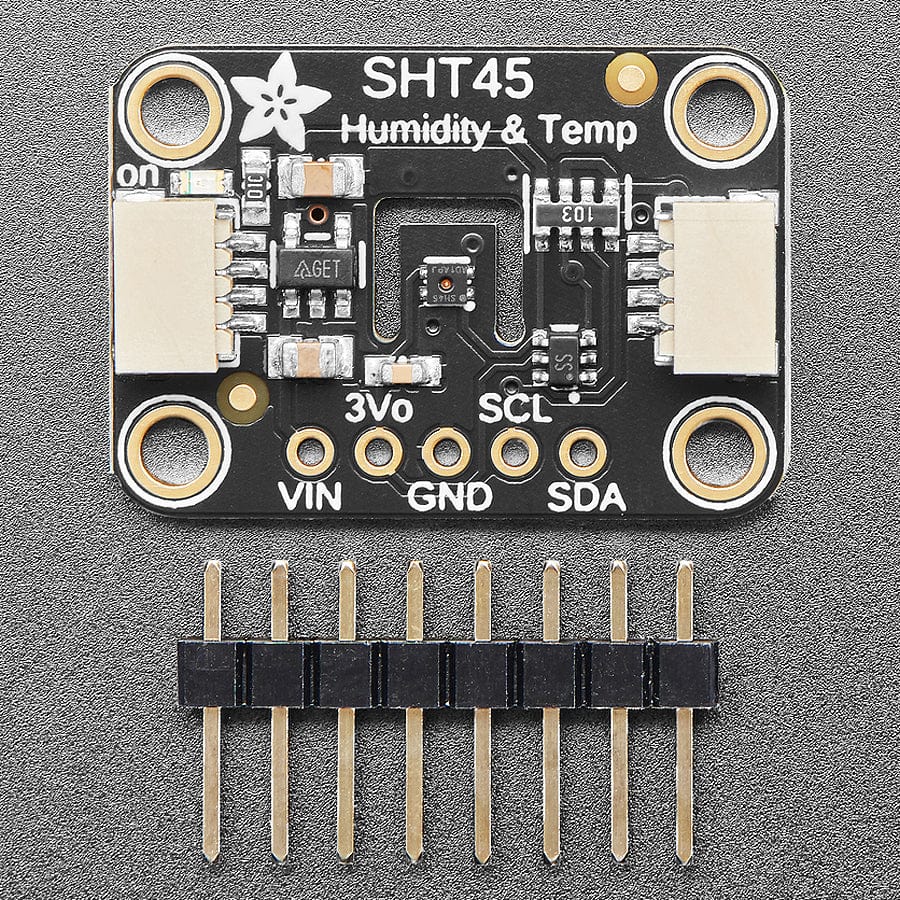
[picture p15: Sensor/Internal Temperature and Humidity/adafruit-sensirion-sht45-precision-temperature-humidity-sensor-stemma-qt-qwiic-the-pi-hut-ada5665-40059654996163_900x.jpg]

</p>

<p align="center"><b>Figure 1:</b> SHT45 Precision Temperature & Humidity Sensor</p>

---

# 3. Hardware Connections

The SHT45 communicates via the **I2C interface**.

## STM32 ↔ SHT45 Connections

| SHT45 Pin | STM32 / System | Description       |
|-----------|-----------------|-------------------|
| VCC       | 3.3V / 5V       | Module power      |
| GND       | GND             | Common ground     |
| SCL       | I2C_SCL         | I2C clock line    |
| SDA       | I2C_SDA         | I2C data line     |

---

## Example STM32F401 Pin Mapping

| STM32 Pin | Peripheral | Function  |
|-----------|------------|-----------|
| PB6       | I2C1_SCL   | I2C clock |
| PB7       | I2C1_SDA   | I2C data  |

---

# 4. API

## Initialisation

| Function | Description |
|----------|-------------|
| `bool SHT4x_Init(I2C_HandleTypeDef *hi2c)` | Initialises the driver with the STM32 I2C peripheral, sets default address/precision/heater settings, and performs a soft reset. Returns `true` on success. |

---

## Important `#define` Constants

These constants are held in `SHT4x.h` and define the I2C address, command bytes, and timeout used by the driver. It may be worth reviewing these before compiling for a different project.

| Variable | Description |
|----------|-------------|
| `SHT4X_DEFAULT_ADDR` | 7-bit I2C address (0x44) shifted for HAL use. |
| `SHT4X_I2C_TIMEOUT_MS` | HAL I2C timeout in milliseconds, used for all I2C transmit/receive calls. |
| `SHT4X_CMD_NOHEAT_HIGH/MED/LOW` | Measurement commands for high/medium/low precision with the heater disabled. |
| `SHT4X_CMD_*HEAT_*` | Measurement commands that enable the on-chip heater at high/medium/low power for 1 s or 100 ms, used for de-icing/de-humidifying the sensor. |
| `SHT4X_CMD_READ_SERIAL` | Command to read the sensor's 32-bit serial number. |
| `SHT4X_CMD_SOFT_RESET` | Command to perform a soft reset of the sensor. |

---

## Public Functions

| Function | Description |
|----------|-------------|
| `bool SHT4x_Init(I2C_HandleTypeDef *hi2c)` | Initialises the driver and performs a soft reset of the sensor. |
| `bool SHT4x_Reset(void)` | Performs a soft reset of the sensor. |
| `bool SHT4x_ReadSerial(uint32_t *serial)` | Reads the sensor's 32-bit serial number with CRC verification. |
| `void SHT4x_SetPrecision(SHT4x_Precision_t precision)` | Sets the measurement precision (affects conversion time and accuracy). |
| `SHT4x_Precision_t SHT4x_GetPrecision(void)` | Returns the current precision setting. |
| `void SHT4x_SetHeater(SHT4x_Heater_t heater)` | Sets the on-chip heater mode, used for de-icing/de-humidifying the sensor. |
| `SHT4x_Heater_t SHT4x_GetHeater(void)` | Returns the current heater mode. |
| `bool SHT4x_GetEvent(SHT4x_Data_t *data)` | Triggers a measurement and returns temperature (°C) and humidity (%RH) in `data`. |

---

# 5. Enums and Structs

## `SHT4x_Precision_t`

Sets the measurement precision, which affects the conversion time and accuracy of each reading.

| Value | Description |
|-------|-------------|
| `SHT4X_HIGH_PRECISION` | Highest accuracy, ~10 ms conversion time. |
| `SHT4X_MED_PRECISION` | Medium accuracy, ~5 ms conversion time. |
| `SHT4X_LOW_PRECISION` | Lowest accuracy, ~2 ms conversion time. |

## `SHT4x_Heater_t`

Sets the on-chip heater, used to clear condensation or ice from the sensor in cold/humid environments.

| Value | Description |
|-------|-------------|
| `SHT4X_NO_HEATER` | Heater disabled (default, normal operation). |
| `SHT4X_HIGH_HEATER_1S` | High heater power, 1 second pulse. |
| `SHT4X_HIGH_HEATER_100MS` | High heater power, 100 ms pulse. |
| `SHT4X_MED_HEATER_1S` | Medium heater power, 1 second pulse. |
| `SHT4X_MED_HEATER_100MS` | Medium heater power, 100 ms pulse. |
| `SHT4X_LOW_HEATER_1S` | Low heater power, 1 second pulse. |
| `SHT4X_LOW_HEATER_100MS` | Low heater power, 100 ms pulse. |

## `SHT4x_Data_t`

Struct used to return sensor readings.

| Member | Description |
|--------|-------------|
| `float temperature` | Temperature in degrees Celsius. |
| `float humidity` | Relative humidity in %RH, clamped to the range 0–100. |

---

# 6. Code Flow

## Processing Steps

1. **Initialisation (run once)**
   - Resets internal driver state
   - Sets default I2C address, precision, and heater mode
   - Performs a soft reset of the sensor

2. **Measurement**
   - Selects the measurement command and conversion delay based on the configured precision and heater mode
   - Sends the measurement command over I2C
   - Waits for the conversion time to elapse
   - Reads 6 bytes back: `[T_MSB, T_LSB, T_CRC, RH_MSB, RH_LSB, RH_CRC]`
   - Verifies the CRC-8 checksum for both the temperature and humidity values

3. **Conversion**
   - Converts raw temperature ticks to degrees Celsius: `T = -45 + 175 * (ticks / 65535)`
   - Converts raw humidity ticks to %RH: `RH = -6 + 125 * (ticks / 65535)`
   - Clamps humidity to the range 0–100 %RH
   - Stores the results internally and returns them via the output struct

---

# 7. Dependencies

- STM32 HAL Library
- STM32 I2C Peripheral

The correct HAL header is included directly in `SHT4x.h` (`stm32f4xx_hal.h`). If targeting a different STM32 family, update this include accordingly (e.g. `stm32l4xx_hal.h`, `stm32h7xx_hal.h`).

---

# 8. Example Usage (C)

```c
SHT4x_Data_t debug_data = {0};

if (!SHT4x_Init(&hi2c3)) {
    Error_Handler();
}

while (1)
{
    if (SHT4x_GetEvent(&debug_data))
    {
        float debug_temperature = debug_data.temperature;
        float debug_humidity    = debug_data.humidity;
    }

    BSP_LED_Toggle(LED_GREEN);
    HAL_Delay(500);
}
```

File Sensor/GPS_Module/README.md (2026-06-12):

# GPS Module Driver (STM32)

# 1. About

This directory contains the driver used to interface with the **Adafruit Ultimate GPS module** for the buoy project.

The GPS module allows the system to monitor the **location of the buoy**, which may change rapidly due to ocean currents or drifting ice. The GPS also provides an accurate **UTC time reference**, which is used to synchronize the buoy's internal timers and periodically poll environmental sensors.

Additional information such as:

- Buoy speed
- Altitude
- Course direction
- Number of satellites in view

can also be obtained from the GPS module.

The GPS data is transmitted using **NMEA sentences over UART**, which are parsed and stored in a global data structure for use by the rest of the system.

---

# 2. Part Information

The GPS module used is the **Adafruit Ultimate GPS Module**, which can be purchased using the link below.

The module contains a **ceramic antenna** that works well in ideal conditions. However, for this project an **external GPS antenna** is used to improve signal reliability when the buoy is deployed in harsh environments.

To use the external antenna, a **uFL to SMA adapter** is required.

**Product Links**

+ Adafruit GPS Module: https://www.adafruit.com/product/746
+ GPS External Antenna: https://www.adafruit.com/product/960
+ Antenna Adapter: https://www.adafruit.com/product/851

<p align="center">
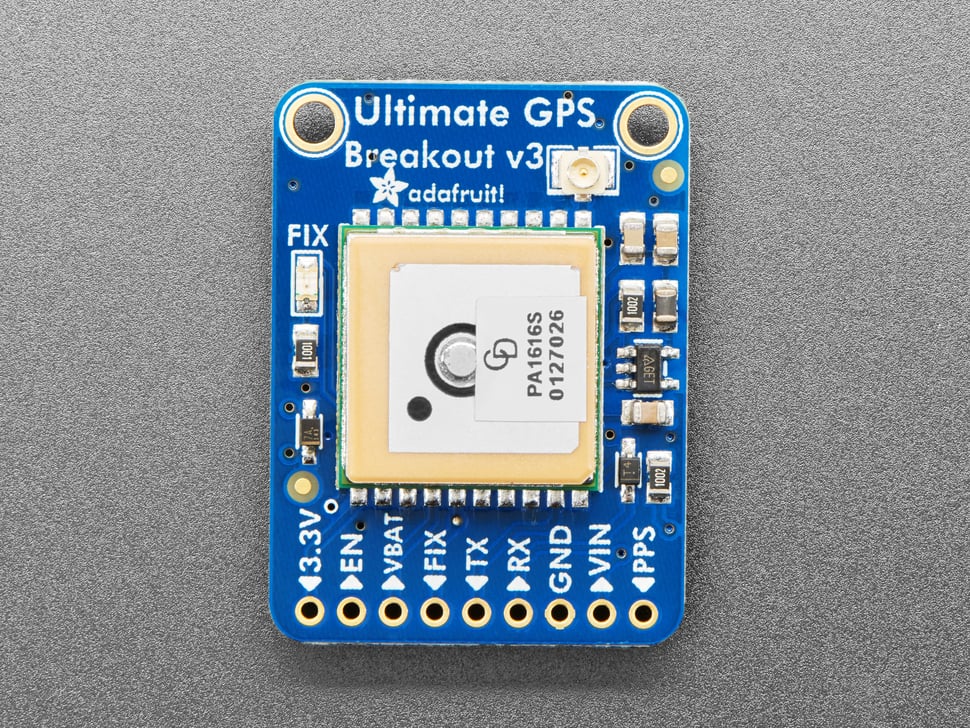
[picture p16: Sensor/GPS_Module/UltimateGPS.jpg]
Adafruit Ultimate GPS Module
  
</p>

<p align="center">Figure 1: Adafruit Ultimate GPS Module</p>

---

# 3. Tested Hardware

This driver has been tested with:

- **STM32F401RCT6**
- **Adafruit Ultimate GPS Module**

---

# 4. Development Environment

The driver was developed using the following environment:

| Tool | Version |
|-----|--------|
| IDE | STM32CubeIDE |
| Version | 2.0.0 |
| Build | 26820_20251114_1348 |
| Vendor | STMicroelectronics |
| MCU | STM32F401RCT6 |
| Firmware Library | STM32 HAL |

---

# 5. Hardware Connections

The Adafruit Ultimate GPS module communicates with the STM32 using a **UART interface**.

The module outputs **NMEA sentences** which contain information such as time, position, speed, and satellite status.

## STM32 ↔ GPS Connections

| GPS Pin | STM32 Peripheral | Description |
|-------|------|-------------|
| VCC | 3.3V | Power supply |
| GND | GND | Ground |
| TX | UART_RX | GPS transmits NMEA data to STM32 |
| RX | UART_TX | STM32 sends configuration commands |
| EN | GPIO | Enables or disables the GPS module |

---

## Example STM32F401 Pin Mapping

| STM32 Pin | Peripheral | Function |
|-----------|-----------|----------|
| PB6 | UART1_TX | UART TX used to send commands |
| PB7 | UART1_RX | UART RX used to receive NMEA strings |
| PB9 | GPIO Output | Enable/disable GPS module |

---

# 6. API

## Functions

| Header | Function | Description |
|------|------|-------------|
| `gps.h` | `void gps_off(const GPS_HandleTypeDef *GPS_PINS)` | Turns off the GPS module |
| `gps.h` | `void gps_on(const GPS_HandleTypeDef *GPS_PINS)` | Turns on the GPS module |
| `gps.h` | `GPS_Status get_gps_data_timed(const GPS_HandleTypeDef *gps_pins)` | Attempts to acquire GPS data for a fixed duration using a timer (useful for cold starts in low power systems) |
| `gps.h` | `GPS_Status get_gps_data(const GPS_HandleTypeDef *gps_pins)` | Attempts to read GPS data once. Typically used when the GPS module is already running (warm start). |

---

# 7. Data Types (Structs)

## GPS_HandleTypeDef

| Type | Field | Description |
|-----|-----|-------------|
| `GPIO_TypeDef *` | `port` | GPIO port used for the enable pin |
| `uint16_t` | `pin` | GPIO pin used for the enable pin |
| `UART_HandleTypeDef *` | `uart` | UART interface connected to the GPS module |
| `TIM_HandleTypeDef *` | `tim` | Timer used by `get_gps_data_timed()` |

---

## GPS_DataTypeDef

When `gps.h` is included, a **global instance** of `GPS_DataTypeDef` called `GPS` is created.  
The GPS driver functions populate this structure with the latest parsed GPS data.

| Type | Field | Description |
|-----|-----|-------------|
| `GPS_Status` | `status` | Indicates whether GPS data acquisition was successful |
| `volatile uint8_t` | `buffer[100]` | Buffer storing the raw NMEA string |
| `volatile uint8_t` | `index` | Internal buffer index (not intended for user access) |
| `char *` | `token[10]` | Used internally for parsing the NMEA sentence |
| `char` | `time[10]` | Stores UTC time |
| `char` | `position[4][10]` | Stores latitude and longitude |
| `char` | `date[10]` | Stores date |
| `char` | `speed_knots[10]` | Speed in knots |
| `char` | `course[10]` | Course direction |
| `char` | `speed_kmh[10]` | Speed in kilometres per hour |
| `char` | `altitude[10]` | Altitude |

---

# 8. Macros

| Header | Macro | Description |
|------|------|-------------|
| `gps.h` | `DURATION` | Determines how many timer periods `get_gps_data_timed()` will run before stopping |

---

# 9. Enums

## GPS_Status

Used for debugging and to indicate the state of GPS data acquisition.

| Value | Description |
|------|-------------|
| `GPS_OK` | GPS command executed successfully |
| `GPS_POSITION_ACQUIRED` | GPS module obtained a valid satellite fix |
| `GPS_POSITION_NOT_ACQUIRED` | GPS module did not obtain a position fix |
| `GPS_OTHER_ACQUIRED` | Other data received but position not available |
| `GPS_ERROR_CHECKSUM` | Received NMEA sentence failed checksum validation |
| `GPS_ERROR_NMEA` | Error reading NMEA string from UART |
| `GPS_ERROR_BUFFER` | NMEA string exceeded buffer length |

---

# 10. Code Flow

For detailed information about individual functions, refer to the **header files**, which contain documentation describing parameters and return values.

An example implementation is provided in the **Example folder**, using an **STM32F401RCT6** with the **HAL driver library**.

<p align="center">
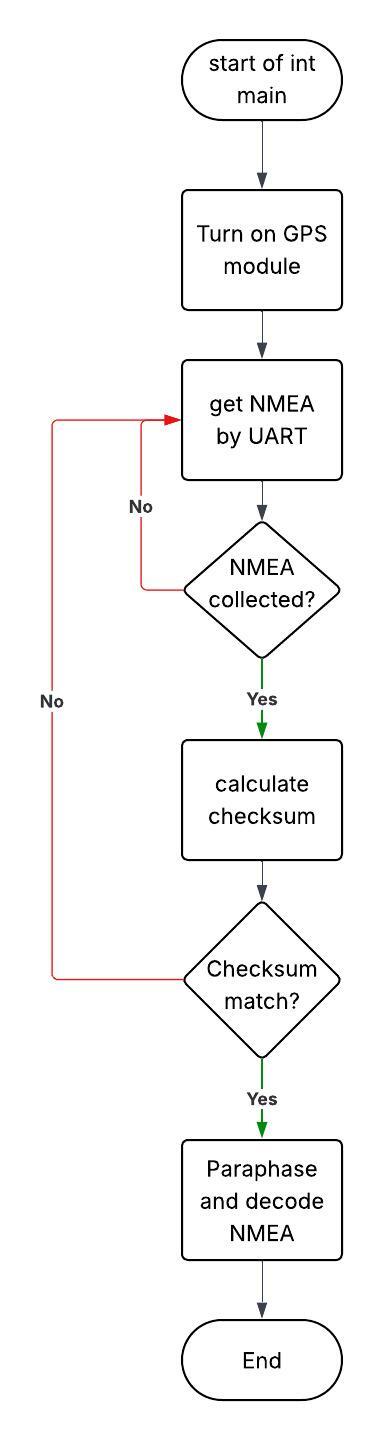
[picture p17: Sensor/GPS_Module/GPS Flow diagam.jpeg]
GPS processing flow diagram
  
</p>

<p align="center">Figure 2: GPS data processing pipeline</p>

### Processing Pipeline

1. Turn on the GPS module  
2. Receive NMEA data via UART  
3. Perform checksum verification  
4. Parse the NMEA sentence  
5. Store decoded data in the global `GPS` structure  

**Note:** This process is encapsulated within the functions  
`get_gps_data_timed(..)` and `get_gps_data(..)`.

---

# 11. Dependencies

This driver requires:

- **STM32 HAL library**
- **UART peripheral**
- **Timer peripheral** (only required when using `get_gps_data_timed()`)

---

# 12. Example Usage

Example initialization and usage:

```c
GPS_HandleTypeDef gps_pins = {
    .port = GPIOB,
    .pin = GPIO_PIN_9,
    .uart = &huart1,
    .tim = &htim1
};

get_gps_data_timed(&gps_pins);
```

---

# 13. Notes

- The driver is designed for **low-power embedded systems**
- The GPS module may require several seconds to minutes to obtain a **cold start satellite fix**
- The `DURATION` macro in `gps.h` can be tuned depending on how long the system should wait for a GPS fix
- External antennas improve reliability in environments with poor satellite visibility

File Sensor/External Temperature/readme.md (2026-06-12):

# External Temperature (STM32)

---

# 1. Overview

A custom made external temperature sensor was made for the buoy that allowed 360 degree external temperature monitoring, while allowing the buoy to be sealant and waterproof.

The sensor itself used a PS103J2 thermistor. This was then placed inside a hollowed out coach bolt. The bolt was then filled with thermal paste to maximise thermal transfer between the bolt and the thermistor, and the thermistor was then fixed in place with resin and heatshrink. A diagram of this is shown below.

<p align="center">
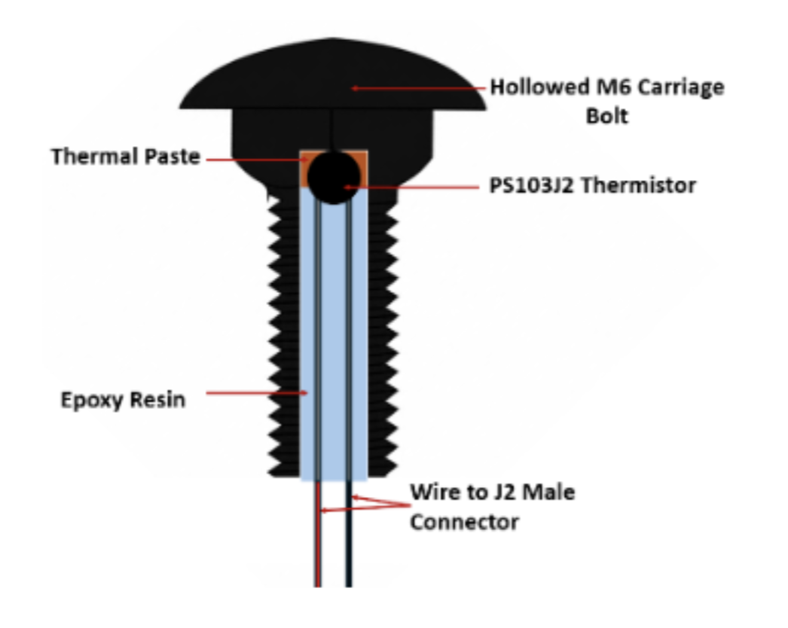
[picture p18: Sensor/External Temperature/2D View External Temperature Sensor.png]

</p>

<p align="center"><b>Figure 1:</b> 2D View of Custom Made External Temperature Sensor.</p>

The thermistors were connected to small JST connectors (1.25mm). These small connectors allowed a nut to easily pass each temperature sensor, allowing it to be secured to the buoy. Each sensor (4 in total) then plugged into a custom made Donut Temperature PCB shown below. This allowed all of them to combine onto one header, so one wire could go from the Donut PCB to the daughterboard to read all the external temperature sensors. This helped reduce wiring in the buoy and supported the buoy design philosophy of allowing every external temperature sensor to be modular and easy to assemble.

<p align="center">
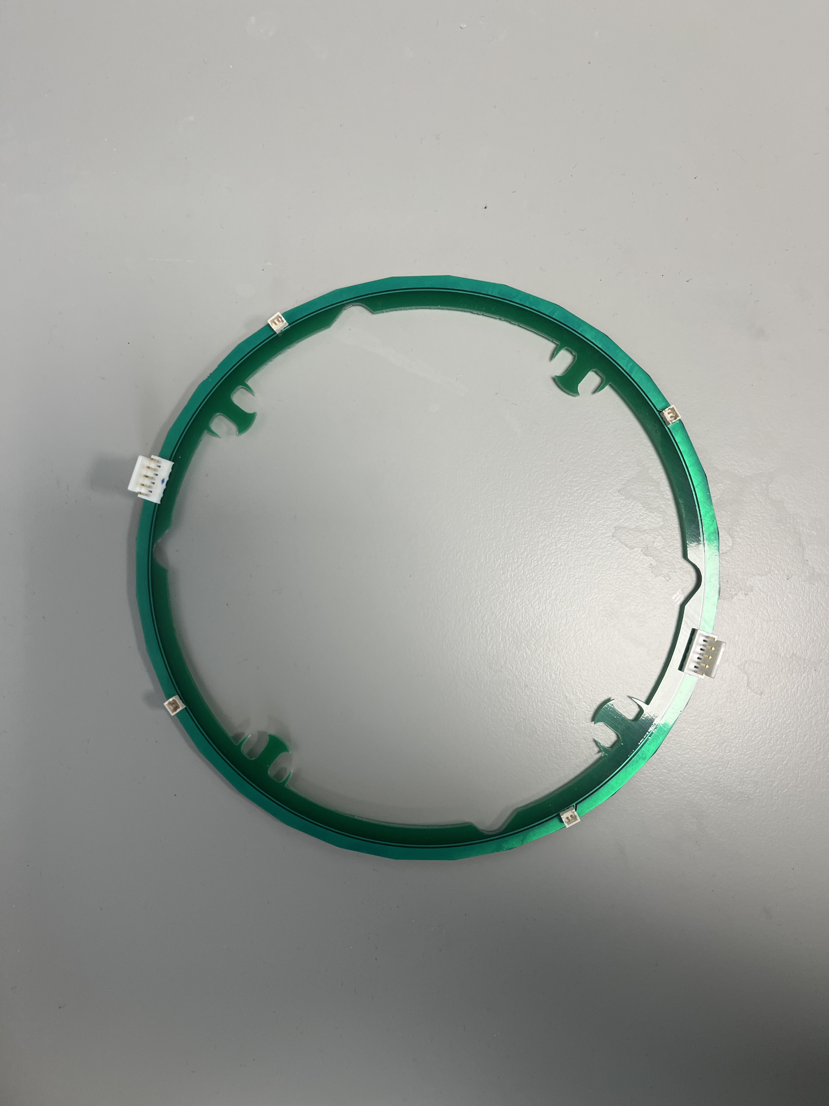
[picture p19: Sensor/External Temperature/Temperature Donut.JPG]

</p>

<p align="center"><b>Figure 2:</b> Custom made Temperature PCB</p>

3.3V from the Donut PCB goes into the thermistors. Each thermistor then connects to the simplified circuit below, which is on the daughter PCB. 3.3V goes into the thermistor, which forms a potential divider with a 15kΩ resistor and 100nF capacitor; this is then fed into an ADC channel on the STM32 as shown in the simplified diagram below.

<p align="center">
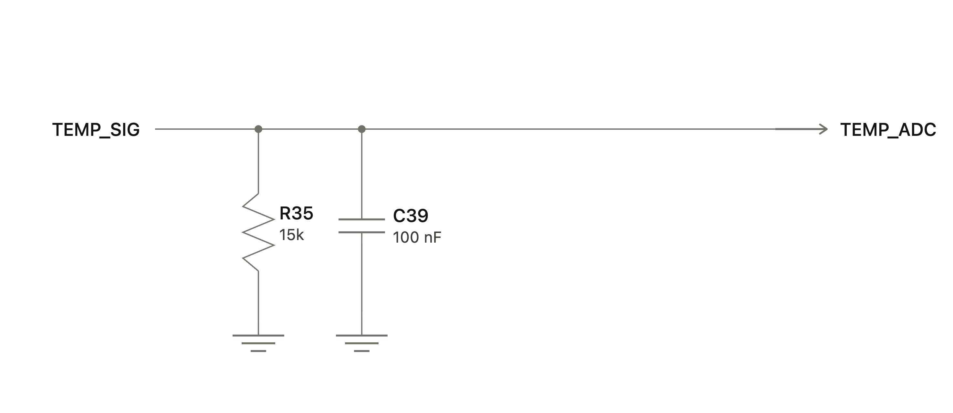
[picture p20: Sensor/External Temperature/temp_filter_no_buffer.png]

</p>

<p align="center"><b>Figure 3:</b> Simplified Thermistor Circuit.</p>

---

# 2. Hardware

The system uses the:

**PS103J2 (NTC Thermistor)**

### Product Link
https://www.digikey.co.uk/en/products/detail/littelfuse-inc/ps103j2/1014531

### Datasheet
https://www.littelfuse.com/assetdocs/littelfuse-leaded-thermistors-standard-precision-ps-datasheet?assetguid=f2c5cde0-806d-4632-bdd3-5e56183e2fd4

<p align="center">
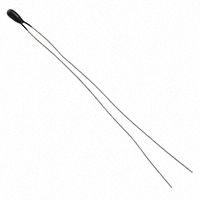
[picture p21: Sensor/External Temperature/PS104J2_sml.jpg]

</p>

<p align="center"><b>Figure 4:</b> PS103J2 NTC Thermistor</p>

---

# 3. CubeMX Setup

As there are 4 analogue external temperature sensors and only 3 ADC channels available on the STM32F405RGT6 (one used for testing), and each sensor needs to be read quickly, some alternative setup in CubeMX is required. If your STM32 has more channels available then you can set up the thermistors normally.

For this project, one ADC channel was used to get around the channel shortage. Each instance of this channel was assigned a rank, set to 480 cycles, and put into scan conversion mode. In the code, ADC reconfiguration is used in the functions to reset the ADC before reading it — this is also why there are a lot of small delays in the code.

A screenshot of how 2 instances of the same ADC channel are set up is shown below. Note this image was taken before the code and system were all switched to 1 ADC channel with 4 instances, but you just keep adding ranks in the settings in the same way.

<p align="center">
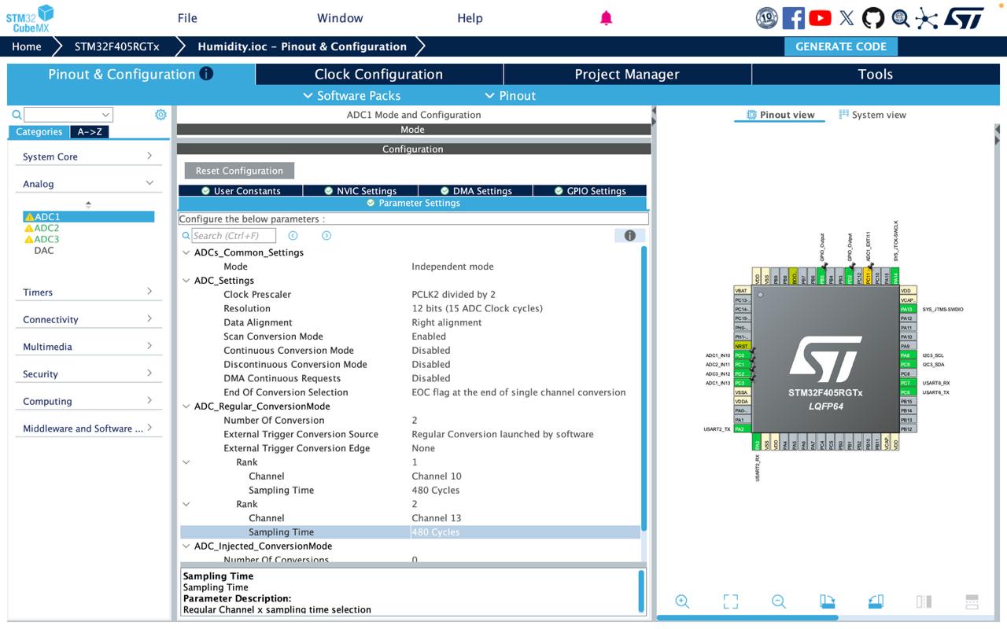
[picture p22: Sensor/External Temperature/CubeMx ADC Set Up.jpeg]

</p>

<p align="center"><b>Figure 5:</b> ADC Setup</p>

---

# 4. Hardware Connections

The thermistors are read via the **STM32 ADC** (analogue input), not I2C.

## STM32 ↔ Thermistor Connections

| Thermistor Circuit Pin | STM32 / System | Description                          |
|-------------------------|-----------------|---------------------------------------|
| 3.3V                    | 3.3V            | Supply to the potential divider        |
| Divider output          | ADC1_INx        | Analogue voltage proportional to temp  |
| GND                     | GND             | Common ground                          |

## STM32F405RGT6 Pin Mapping

| STM32 Pin | Peripheral | Function                  |
|-----------|------------|---------------------------|
| PC0       | ADC1_IN10  | Thermistor channel 1       |
| PC1       | ADC1_IN11  | Thermistor channel 2       |
| PC2       | ADC1_IN12  | Thermistor channel 3       |
| PC3       | ADC1_IN13  | Thermistor channel 4       |

**Note:** PC0 is configured as analogue by default via `MX_ADC1_Init()`. PC1, PC2, and PC3 must also be set to `GPIO_MODE_ANALOG` in the `.ioc` file for all four channels to be usable.

---

# 5. API

## Initialisation

| Function | Description |
|----------|-------------|
| `void temp_sensor_init(void)` | Overrides the `MX_ADC1_Init()` scan configuration to single-conversion mode, which is required for per-channel dynamic switching in `temp_sensor_read()`. Must be called after `MX_ADC1_Init()` and before `sensors_init()`. |

---

## Important `#define` Constants

| Variable | Description |
|----------|-------------|
| `TEMPERATURE_ERROR_SENTINEL` | Value (`-99.9f`) returned for any channel that fails to produce a valid reading. |

---

## Public Functions

| Function | Description |
|----------|-------------|
| `void temp_sensor_init(void)` | Reconfigures ADC1 into single-conversion mode for per-channel reads. |
| `void temp_sensor_read(uint8_t *out, uint8_t *len_out)` | Reads all four thermistor channels sequentially and writes 4 × float32 temperatures (°C) into `out`. `out` must be at least 16 bytes. `len_out` is set to 16 and may be `NULL`. |

---

# 6. Code Flow

## Processing Steps

1. **Initialisation (run once)**
   - Reconfigures ADC1 from scan mode to single-conversion mode
   - Prepares the driver for sequential per-channel reads

2. **Measurement**
   - Reconfigures and triggers ADC1 for each thermistor channel (PC0–PC3 / ADC1_IN10–IN13) in turn
   - Small delays are used between reconfigurations to allow the ADC to settle
   - Reads the raw ADC value for each channel

3. **Conversion & Output**
   - Converts each channel's raw ADC reading to a temperature in °C using the thermistor's resistance/temperature relationship
   - Any channel that fails to produce a valid reading is set to `TEMPERATURE_ERROR_SENTINEL` (-99.9°C)
   - Writes all 4 channel temperatures as float32 values into the output buffer (16 bytes total)

---

# 7. Dependencies

- STM32 HAL Library
- STM32 ADC1 Peripheral

---

# 8. Example Usage (C)

```c
uint8_t  ext_temp_buf[16];
uint8_t  ext_temp_len = 0;

temp_sensor_init();   // call after MX_ADC1_Init(), before sensors_init()

while (1)
{
    temp_sensor_read(ext_temp_buf, &ext_temp_len);

    float ch1, ch2, ch3, ch4;
    memcpy(&ch1, &ext_temp_buf[0],  4);
    memcpy(&ch2, &ext_temp_buf[4],  4);
    memcpy(&ch3, &ext_temp_buf[8],  4);
    memcpy(&ch4, &ext_temp_buf[12], 4);

    BSP_LED_Toggle(LED_GREEN);
    HAL_Delay(500);
}
```

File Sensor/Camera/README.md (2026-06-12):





# Camera Driver – Arducam OV2640 (STM32)

---

# 1. About

This directory contains a **C driver for the Arducam 2MP OV2640 camera module**, designed to run on **STM32 microcontrollers**.

The driver was developed as part of the **Prototype Climate Monitoring Sensor Buoy project**, where the system periodically captures images to monitor environmental conditions.

The implementation supports:

- OV2640 sensor configuration via **I2C**
- Image capture using the **Arducam FIFO**
- Image transfer via **SPI**
- **JPEG decoding** using **TJpgDec**
- Basic **image quality analysis** (brightness, variance, saturation)

---

# 2. Hardware

This project uses the **Arducam Mini 2MP SPI Camera Module with OV2640 sensor**.

<p align="center">
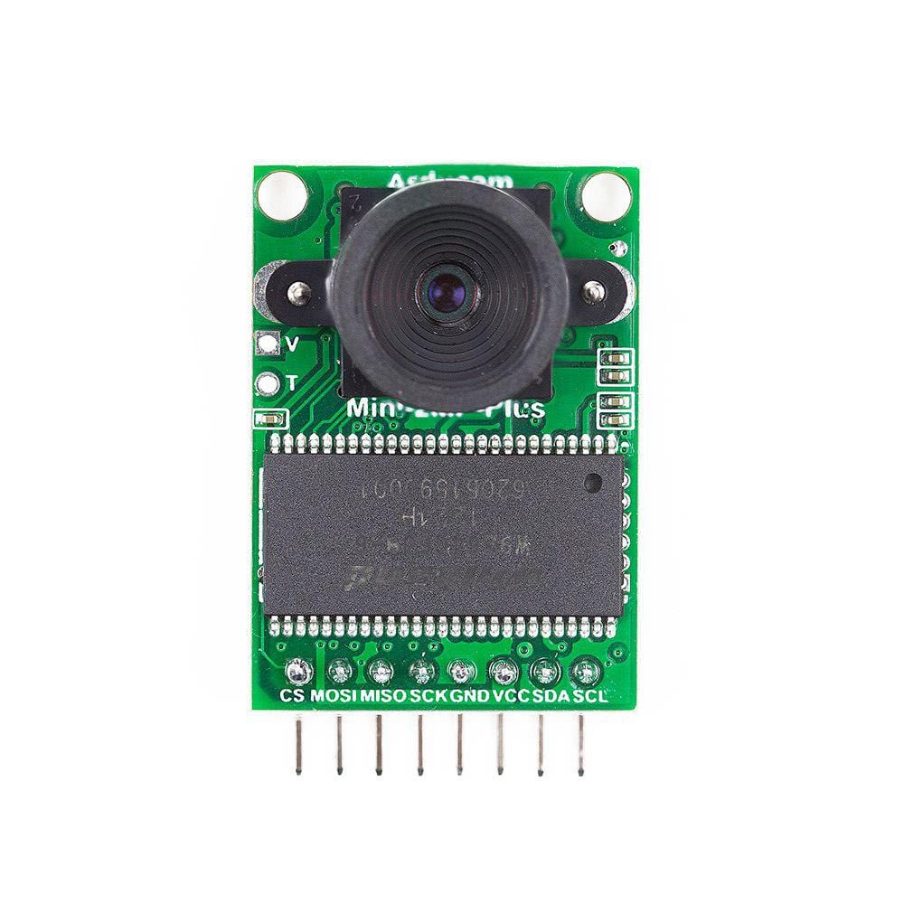
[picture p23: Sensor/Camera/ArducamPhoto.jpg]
Arducam camera module
  
</p>

<p align="center">Figure 1: Arducam Mini 2MP OV2640 Camera Module</p>

**Product link:**  
https://thepihut.com/products/mini-2mp-spi-camera-module-for-raspberry-pi-pico

The module contains:

- **OV2640 CMOS image sensor**
- **Arducam FIFO image buffer**
- **SPI interface for image transfer**
- **I2C interface for sensor configuration**

---

# 3. Tested Hardware

This driver has been tested with:

- **STM32F401RCT6**
- **Arducam Mini 2MP SPI Camera (OV2640)**

---

# 4. Development Environment

| Tool | Version |
|-----|--------|
| IDE | STM32CubeIDE |
| Version | 2.0.0 |
| Build | 26820_20251114_1348 |
| Vendor | STMicroelectronics |
| MCU | STM32F401RCT6 |
| Firmware Library | STM32 HAL |

---

# 5. Hardware Connections

The Arducam module communicates with the STM32 using **SPI for image data** and **I2C for camera configuration**.

## STM32 ↔ Arducam Connections

| Arducam Pin | STM32 Peripheral | Description |
|-------------|------------------|-------------|
| VCC | 3.3V | Power supply |
| GND | GND | Ground |
| SCL | I2C_SCL | I2C clock used to configure OV2640 registers |
| SDA | I2C_SDA | I2C data line used for sensor configuration |
| MOSI | SPI_MOSI | SPI data from MCU to Arducam |
| MISO | SPI_MISO | SPI data from Arducam FIFO to MCU |
| SCK | SPI_SCK | SPI clock |
| CS | GPIO | Chip select for Arducam SPI interface |

---

## Example STM32F401 Pin Mapping

| STM32 Pin | Peripheral | Function |
|-----------|-----------|----------|
| PB3 | SPI1_SCK | SPI clock |
| PB4 | SPI1_MISO | SPI data from camera |
| PB5 | SPI1_MOSI | SPI data to camera |
| PB6 | I2C1_SCL | I2C clock |
| PB7 | I2C1_SDA | I2C data |
| PB9 | GPIO Output | Arducam Chip Select |

---

# 6. API

## Functions

| Header | Function | Description |
|------|------|-------------|
| `ArducamOV2640.h` | `upload_ov2640_settings(const CameraTypeDef *camera_pins, const SensorReg *set_resolution)` | Resets the OV2640 and uploads initialization, JPEG, and resolution configuration settings |
| `ArducamOV2640.h` | `CameraStatus capture(const CameraTypeDef *camera_pins)` | Captures a JPEG image from the OV2640 sensor |
| `ArducamOV2640.h` | `CameraStatus burst_read(const CameraTypeDef *camera_pins, uint8_t *image_buffer)` | Reads JPEG bytes from the Arducam FIFO buffer over SPI |
| `ArducamOV2640.h` | `uint32_t true_length_of_jpeg(const CameraTypeDef *camera_pins, const uint8_t *image_buffer)` | Calculates the true JPEG size by detecting JPEG start/end markers |
| `jpeg_decode.h` | `JpegStatus jpeg_decode(JpegInformation *jpeg)` | Decodes JPEG data into a grayscale image using TJpgDec |
| `image_quality.h` | `ImageStatus image_processing(const JpegInformation *jpeg, ImageQualityInformation *image)` | Calculates image metrics and evaluates image quality |

---

# 7. Data Types (Structs)

## `CameraTypeDef`

Defined in **ArducamOV2640.h**

| Type | Field | Description |
|-----|-----|-------------|
| `GPIO_TypeDef *` | `port` | GPIO port used for SPI chip select |
| `uint16_t` | `pin` | GPIO pin used for SPI chip select |
| `I2C_HandleTypeDef *` | `i2c` | I2C interface connected to the OV2640 sensor |
| `SPI_HandleTypeDef *` | `spi` | SPI interface connected to the Arducam FIFO |

---

## `JpegInformation`

Defined in **jpeg_decode.h**

| Type | Field | Description |
|-----|-----|-------------|
| `uint16_t` | `width` | Image width used during decoding |
| `uint16_t` | `height` | Image height used during decoding |
| `uint8_t` | `grey_image_buffer[RESOLUTION_WIDTH * RESOLUTION_HEIGHT]` | Output grayscale image buffer |
| `uint8_t` | `work_buffer[4096]` | Temporary buffer used internally by TJpgDec |
| `uint8_t` | `data[MAX_IMAGE_SIZE]` | Raw JPEG image buffer |
| `uint32_t` | `size` | Size of the JPEG image |
| `size_t` | `position` | Current read position used by the decoder |

---

## `ImageQualityInformation`

Defined in **image_quality.h**

| Type | Field | Description |
|-----|-----|-------------|
| `uint32_t` | `saturation_low_val` | Number of underexposed pixels |
| `uint32_t` | `saturation_high_val` | Number of overexposed pixels |
| `float` | `variance_val` | Image variance (texture/spread) |
| `ImageStatus` | `suitability_val` | Result of image quality evaluation |
| `uint8_t` | `mean_val` | Average brightness of the image |

---

# 8. Macros

| Header | Macro | Description |
|------|------|-------------|
| `jpeg_decode.h` | `MAX_IMAGE_SIZE` | Maximum size of the JPEG image buffer |
| `jpeg_decode.h` | `RESOLUTION_WIDTH` | Image width used for decoding |
| `jpeg_decode.h` | `RESOLUTION_HEIGHT` | Image height used for decoding |
| `image_quality.h` | `MEAN_UPPER_THRESHOLD` | Maximum brightness threshold |
| `image_quality.h` | `MEAN_LOWER_THRESHOLD` | Minimum brightness threshold |
| `image_quality.h` | `VARIANCE_THRESHOLD` | Minimum variance threshold |
| `image_quality.h` | `MAX_SATURATED_HIGH_RATIO` | Maximum allowed percentage of overexposed pixels |
| `image_quality.h` | `MAX_SATURATED_LOW_RATIO` | Maximum allowed percentage of underexposed pixels |
| `image_quality.h` | `PIXEL_OVEREXPOSURE_LIMIT` | Pixel brightness value considered overexposed |
| `image_quality.h` | `PIXEL_UNDEREXPOSURE_LIMIT` | Pixel brightness value considered underexposed |

---

# 9. Supported Resolutions

The OV2640 sensor supports multiple JPEG resolutions.

For this project the firmware is configured for **QQVGA (160×120)** due to the **limited RAM available on the STM32F401RCT6**.

Using higher resolutions requires increasing several buffers in the code:

- `grey_image_buffer`
- `data` (JPEG storage)
- `MAX_IMAGE_SIZE`
- `RESOLUTION_WIDTH`
- `RESOLUTION_HEIGHT`

| Header | Macro | Resolution | Dimensions |
|------|------|-----------|-----------|
| `ov2640_regsV2.h` | `OV2640_160x120_JPEG` | QQVGA | 160 × 120 |
| `ov2640_regsV2.h` | `OV2640_QVGA` | QVGA | 320 × 240 |
| `ov2640_regsV2.h` | `OV2640_640x480_JPEG` | VGA | 640 × 480 |
| `ov2640_regsV2.h` | `OV2640_800x600_JPEG` | SVGA | 800 × 600 |
| `ov2640_regsV2.h` | `OV2640_1024x768_JPEG` | XGA | 1024 × 768 |
| `ov2640_regsV2.h` | `OV2640_1280x1024_JPEG` | SXGA | 1280 × 1024 |
| `ov2640_regsV2.h` | `OV2640_1600x1200_JPEG` | UXGA | 1600 × 1200 |

---

# 10. Memory Usage

Typical RAM usage when operating at **QQVGA (160×120)** resolution:

| Component | RAM Usage |
|----------|-----------|
| JPEG buffer (`data`) | ~8–20 KB |
| Grayscale buffer (`grey_image_buffer`) | 19.2 KB |
| TJpgDec working buffer | 4 KB |
| Image quality structure | ~32 bytes |
| Camera driver state | < 64 bytes |

**Approximate total RAM usage:**  
`~32–45 KB`  

Higher resolutions require increasing:

- `MAX_IMAGE_SIZE`
- `RESOLUTION_WIDTH`
- `RESOLUTION_HEIGHT`
- `grey_image_buffer`

---

# 11. Performance

Typical processing times measured on **STM32F401RCT6**:

| Stage | Approximate Time |
|------|----------------|
| Camera capture | 150 – 300 ms |
| SPI image transfer | 50 – 150 ms |
| JPEG decoding | 200 – 400 ms |
| Image quality processing | < 5 ms |

**Total processing time:** ~400 – 800 ms per captured image  

---

# 12. Enums

## `CameraStatus`

| Value | Description |
|------|-------------|
| `CAMERA_OK` | Operation successful |
| `CAMERA_ERROR_I2C` | I2C communication failure |
| `CAMERA_ERROR_I2C_RESET` | Failed to upload reset configuration |
| `CAMERA_ERROR_I2C_JPEG_INT` | Failed to upload JPEG initialization settings |
| `CAMERA_ERROR_I2C_JPEG` | Failed to upload JPEG compression settings |
| `CAMERA_ERROR_I2C_RESOLUTIONS` | Failed to upload resolution configuration |
| `CAMERA_ERROR_SPI` | SPI communication error |
| `CAMERA_ERROR_TIMEOUT` | Operation timeout |

## `ImageStatus`

| Value | Description |
|------|-------------|
| `IMAGE_OK` | Image suitable for use |
| `IMAGE_BRIGHTNESS_HIGH` | Image too bright |
| `IMAGE_BRIGHTNESS_LOW` | Image too dark |
| `IMAGE_TEXTURE_LOW` | Insufficient variance / texture |
| `IMAGE_SATURATION_HIGH` | Too many overexposed pixels |
| `IMAGE_SATURATION_LOW` | Too many underexposed pixels |

## `JpegStatus`

| Value | Description |
|------|-------------|
| `JPEG_OK` | JPEG successfully decoded |
| `JPEG_ERROR_INIT` | JPEG decoder initialization failed |
| `JPEG_ERROR_DECODE` | General decode error |

---

# 13. Code Flow

<p align="center">
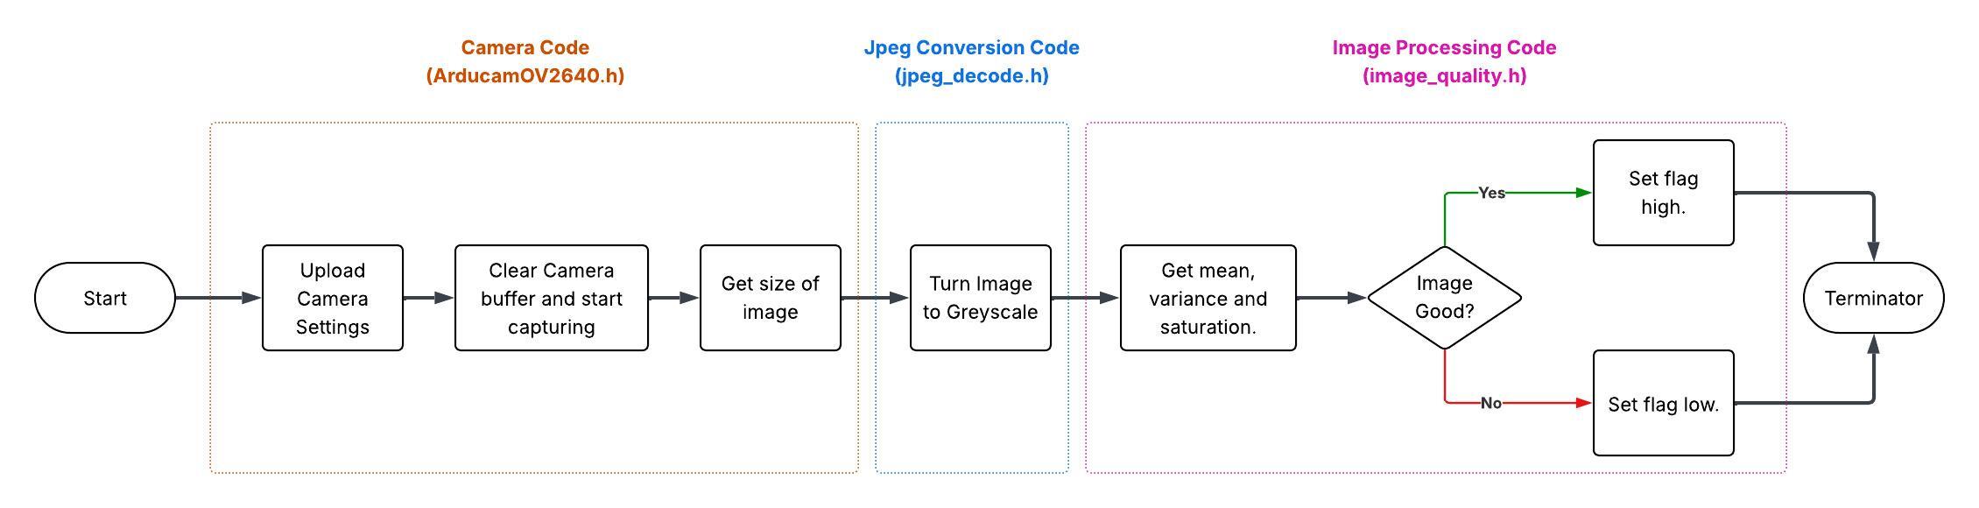
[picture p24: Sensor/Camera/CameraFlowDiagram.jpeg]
Camera processing flow
  
</p>

<p align="center">Figure 2: Camera processing pipeline</p>

### Processing Pipeline

1. Configure the OV2640 sensor via **I2C**
2. Trigger image capture
3. Read JPEG data from the **Arducam FIFO via SPI**
4. Detect the **true JPEG length**
5. Decode the JPEG image to **grayscale**
6. Perform **image quality analysis**

---

# 14. Dependencies

- **STM32 HAL library**
- **TJpgDec** lightweight JPEG decoder
- **SPI and I2C peripherals**

---

# 15. Example Usage

```c
CameraTypeDef camera_pins = {
    .port = GPIOB,
    .pin = GPIO_PIN_9,
    .i2c = &hi2c1,
    .spi = &hspi1
};

JpegInformation jpeg;
ImageQualityInformation image_quality;

upload_ov2640_settings(&camera_pins, OV2640_160x120_JPEG);

capture(&camera_pins);

burst_read(&camera_pins, jpeg.data);

jpeg.size = true_length_of_jpeg(&camera_pins, jpeg.data);

jpeg_decode(&jpeg);

image_processing(&jpeg, &image_quality);

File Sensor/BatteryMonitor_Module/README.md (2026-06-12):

# Battery Monitor Module (STM32)

If you are looking for libraries for **Arduino or Raspberry Pi Pico**, please refer to the official Adafruit documentation:

https://learn.adafruit.com/adafruit-ina219-current-sensor-breakout/arduino-code

---

# 1. Overview

This directory contains a driver for interfacing with the **INA219 High-Side DC Current Sensor** over I2C using an STM32 microcontroller.

The INA219 enables real-time measurement of:
- Bus voltage  
- Current draw  
- Power consumption  

This module is used in the buoy project to monitor battery usage and estimate the **state of charge (SoC)**. Accurate energy monitoring is critical in low-power systems where energy availability is limited.

---

# 2. Hardware

The system uses the:

**INA219 High Side DC Current Sensor Breakout – 26V ±3.2A (STEMMA QT)**

### Product Link
https://www.adafruit.com/product/904

<p align="center">
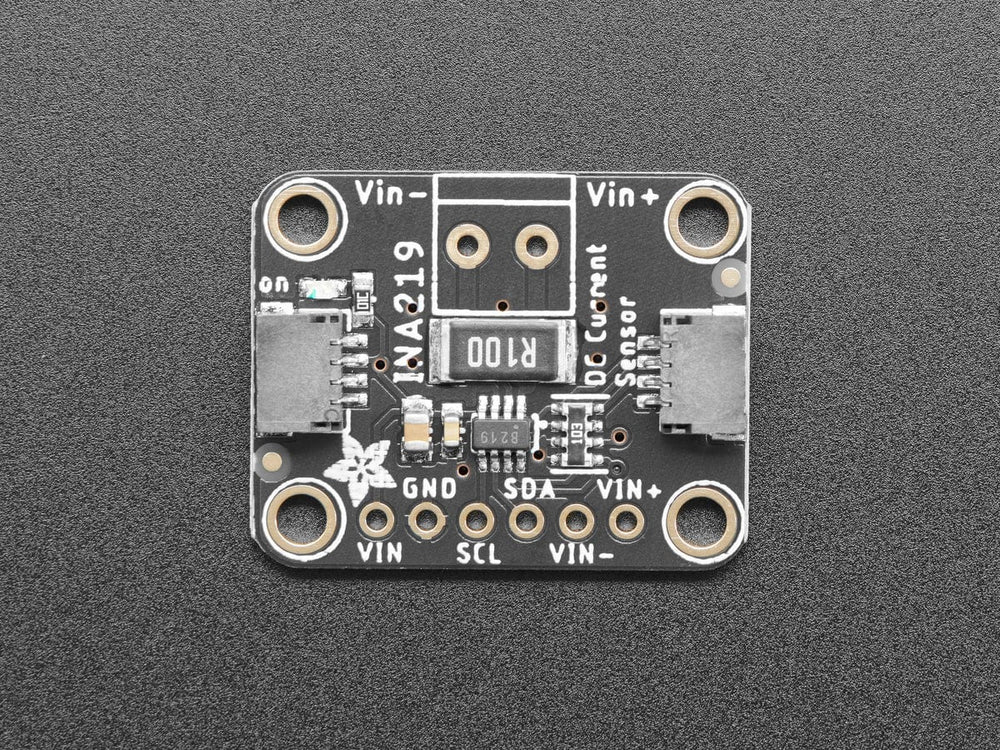
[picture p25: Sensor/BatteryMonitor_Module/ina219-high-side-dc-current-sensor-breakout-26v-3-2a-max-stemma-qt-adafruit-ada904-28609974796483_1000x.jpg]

</p>

<p align="center"><b>Figure 1:</b> INA219 Current Sensor Module</p>

---

# 3. Hardware Connections

The INA219 communicates via the **I2C interface**.

## STM32 ↔ INA219 Connections

| INA219 Pin | STM32 / System | Description                  |
|------------|----------------|------------------------------|
| VCC        | 3.3V           | Module power supply          |
| GND        | GND            | Common ground                |
| SCL        | I2C_SCL        | I2C clock line              |
| SDA        | I2C_SDA        | I2C data line               |
| VIN+       | Battery +      | Connected to battery supply |
| VIN-       | Load +         | Output to system load       |

> ⚠️ Current is measured across the internal shunt resistor between VIN+ and VIN-.

---

## Example STM32F401 Pin Mapping

| STM32 Pin | Peripheral | Function  |
|----------|-----------|----------|
| PB6      | I2C1_SCL  | I2C clock |
| PB7      | I2C1_SDA  | I2C data  |

---

# 4. API

## Constructor

| Function | Description |
|----------|------------|
| `BatteryMonitor(I2C_HandleTypeDef* handle)` | Initialises the driver with the STM32 I2C peripheral. Internal variables are reset during construction. |

---

## Public Functions

| Function | Description |
|----------|------------|
| `BatteryStatus init(float current_temp_c)` | Initialises the sensor, performs calibration, and estimates initial state-of-charge using voltage. |
| `BatteryStatus update(float current_temp_c)` | Updates measurements and state-of-charge using current integration (coulomb counting) with voltage correction. |
| `float get_percentage()` | Returns the latest state-of-charge (%). |
| `float get_voltage()` | Returns the measured bus voltage (V). |
| `float get_current()` | Returns the measured current (mA or A depending on implementation). |

---

# 5. Enums

## `BatteryStatus`

Used for error handling and debugging.

| Value | Description |
|------|------------|
| `BATTERY_OK` | Operation successful |
| `BATTERY_I2C_ERROR` | I2C communication failure |
| `BATTERY_DATA_FAULT` | Invalid or corrupted sensor data |

---

# 6. Code Flow

<p align="center">
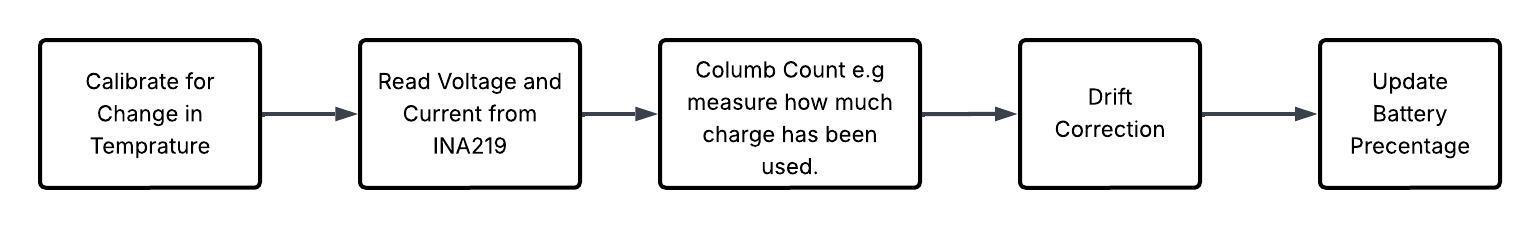
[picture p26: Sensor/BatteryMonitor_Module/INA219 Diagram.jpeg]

</p>

<p align="center"><b>Figure 2:</b> INA219 Processing Pipeline</p>

## Processing Steps

1. **Initialisation (run once)**
   - Sensor calibration  
   - Initial voltage measurement  
   - Estimate initial state-of-charge  

2. **Temperature Compensation**
   - Adjust parameters based on measured temperature  

3. **Measurement**
   - Read bus voltage  
   - Read current  

4. **Coulomb Counting**
   - Integrate current over time to estimate energy usage  

5. **Drift Correction**
   - Apply voltage-based correction to reduce long-term drift  

6. **State Update**
   - Update remaining capacity and percentage  

---

# 7. Dependencies

- STM32 HAL Library  
- STM32 I2C Peripheral  

---

# 8. Example Usage (C++)

```cpp
// Instantiate the battery monitor using I2C handle
BatteryMonitor system_battery(&hi2c3);

float current_buoy_temp = 25.0f;

// Initialise the sensor
BatteryStatus init_status = system_battery.init(current_buoy_temp);

if (init_status != BATTERY_OK) {
    // Handle initialisation error
}

// Main loop
while (1)
{
    float current_buoy_temp = 25.0f;

    if (system_battery.update(current_buoy_temp) == BATTERY_OK) {
        float battery_percentage = system_battery.get_percentage();
        float current_draw       = system_battery.get_current();
        float battery_voltage    = system_battery.get_voltage();

        (void)battery_percentage;
        (void)current_draw;
        (void)battery_voltage;
    } else {
        // Handle errors (I2C or data fault)
    }

    HAL_Delay(500);
}

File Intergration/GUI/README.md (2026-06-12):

# ArcticSense Buoy Monitor — Ground Station GUI

Python/Tkinter ground station for the ArcticSense polar climate monitoring buoy. Communicates with the buoy over Bluetooth Low Energy via the HM-10 UART-transparent module, decodes the sensor payload, and persists readings to CSV.

---

## Setup

```bash
cd GUI
pip3 install bleak Pillow tkintermapview matplotlib
python3 run.py
```

`tkintermapview` is optional — the GPS panel falls back to a text label if it is not installed.  
`matplotlib` is optional — graphs are replaced with a placeholder if it is not installed.  
`Pillow` is required for camera image display.

---

## File layout

```
GUI/
├── run.py                          # entry point — calls buoy_monitor.main()
├── buoy_monitor.py                 # BuoyMonitorApp: main window, BLE callbacks, card updates
├── ble_manager.py                  # BLEManager: BLE scanning, command framing, payload decode
├── data_store.py                   # CSV persistence, metric metadata, ID generation
├── data/
│   └── sensor_readings.csv         # live sensor log (auto-created on first run)
├── images_history/                 # saved JPEG captures, named by metric_id
├── ui/
│   ├── constants.py                # colour palette, fonts, layout dimensions, metric lists
│   ├── mpl_loader.py               # deferred matplotlib import (avoids ~0.5 s startup cost)
│   ├── panels/
│   │   ├── graph_panel.py          # GraphPanel: time-series matplotlib graphs
│   │   ├── camera_panel.py         # camera detail view and image-quality metrics panel
│   │   ├── gps_panel.py            # GPSPanel: tkintermapview live map
│   │   └── data_log_panel.py       # DataLogPanel: By Instance and Flat Table views
│   └── widgets/
│       ├── flat_button.py          # FlatButton: cross-platform styled button
│       └── metric_card.py          # MetricCard: sensor card with checkbox, value, and ID label
└── ArcticSense.png / arcticsenselogo1.png   # window icon and top-bar logo
```

---

## Architecture

```
BuoyMonitorApp (buoy_monitor.py)
│
├─ BLEManager (ble_manager.py)          ← background asyncio loop + Bleak
│   ├─ BLE scanning / connection
│   ├─ Command framing (build_command)
│   ├─ Fragment reassembly (_on_notify)
│   ├─ Sensor payload decode (decode_sensor_payload)
│   └─ Image quality decode (decode_image_metrics)
│
├─ DataStore (data_store.py)            ← CSV on disk
│   ├─ record_reading / record_readings
│   ├─ load_history
│   └─ new_instance_id / build_metric_id
│
└─ UI panels (ui/panels/)               ← Tkinter, all on main thread
    ├─ GraphPanel         matplotlib time-series
    ├─ GPSPanel           tkintermapview live map
    ├─ CameraPanel        image + quality metrics
    └─ DataLogPanel       By Instance / Flat Table
```

### Threading model

| Thread | Role |
|--------|------|
| Main | Tkinter event loop (`root.mainloop()`) |
| BLE thread | asyncio event loop hosting Bleak coroutines |
| Graph thread | matplotlib figure build (one per draw call) |

BLE callbacks fire on the BLE thread. All Tkinter widget updates are marshalled back to the main thread with `root.after(0, callback)`. Direct cross-thread Tkinter calls are unsafe and are not used anywhere in the codebase.

---

## BLE wire protocol

The BLE device name scanned for is **`EnduranceMKII`** (configurable via `HM10_NAME` in `ble_manager.py`).

### Start-of-frame bytes

| Constant | Value | Direction | Meaning |
|----------|-------|-----------|---------|
| `STX_CMD` | `0xAC` | GUI → buoy | Sensor request command |
| `STX_ACK` | `0xFF` | GUI → buoy | Acknowledge after receiving response |
| `STX_SENSOR_MORE` | `0xAA` | buoy → GUI | Sensor data fragment, more follow |
| `STX_SENSOR_LAST` | `0xAF` | buoy → GUI | Sensor data fragment, last |
| `STX_IMG_MORE` | `0xA0` | buoy → GUI | JPEG image fragment, more follow |
| `STX_IMG_LAST` | `0xA1` | buoy → GUI | JPEG image fragment, last |
| `STX_META_MORE` | `0xA2` | buoy → GUI | Image quality metrics fragment, more follow |
| `STX_META_LAST` | `0xA3` | buoy → GUI | Image quality metrics fragment, last |

### Command packet (5 bytes, GUI → buoy)

```
Byte 0 : 0xAC  (STX_CMD)
Byte 1 : mask[7:0]    sensor bitmask, low byte
Byte 2 : mask[15:8]   sensor bitmask, mid byte
Byte 3 : mask[23:16]  sensor bitmask, high byte
Byte 4 : checksum of bytes 0–3
```

### Fragment packet (20 bytes, buoy → GUI)

```
Byte 0     : STX (one of the buoy→GUI values above)
Bytes 1–2  : fragment index (big-endian uint16)
Bytes 3–18 : 16-byte payload chunk
Byte 19    : checksum of bytes 0–18
```

### Firmware sensor bitmask

```
Bit   GUI metric(s)                     Format   Bytes   Notes
---   -----------------------------------  ------  -----   --------------------------
 0    UV Index + Lux                      <ff       8     two float32
 1    Camera 1                            image     –     JPEG stream via STX_IMG_*;
                                                           preceded by STX_META_*
 2    Camera 2                            image     –     same structure as Camera 1
 3    GPS                                 <ii       8     two int32, scale ×1e-6 → °
 4    Tilt (roll, pitch)                  <ff       8     two float32 → °
 5    Battery + Voltage + Current Draw    <fff     12     float32: %, V, mA
 6    EMI I/Q/Magnitude/Phase/PhaseIQ    <fffff   20     five float32
 7    Temp Internal (Dynamic) +
      Humidity (Dynamic)                  <ff       8     two float32: °C, %
11    Temp Internal (Static) +
      Humidity (Static)                   <ff       8     two float32: °C, %
12    Temp External (4-channel)           <4f      16     four float32 → °C
13    Turbidity                           <f        4     float32 → NTU
14    IMU (pitch, roll, yaw)              <3f      12     three float32 → °
15    Salinity                            <H        2     uint16, scale ×0.01 → mS
23    STANDBY_MASK (0x800000)             –         –     keep-alive when mask = 0
```

Sensor fields are packed in the order they appear in `SENSORS` (ble_manager.py), lowest set bit first. Sensors sharing a bit (e.g. UV+Lux on bit 0, Battery trio on bit 5) are consecutive entries in `SENSORS` and are decoded by reading sequentially. Cameras (bits 1, 2) are not in `SENSORS`, they arrive as separate JPEG streams and are handled by `_handle_image_payload`.

---

## Camera image quality

Before each JPEG, the firmware sends a 22-byte quality-metrics packet. The GUI decodes it with `decode_image_metrics()` and displays a pass/fail panel below the image in the camera detail view.

| Metric | Key | Pass threshold |
|--------|-----|---------------|
| Laplacian Variance | `lapvar` | > 4297.0 |
| Histogram Entropy | `entropy` | > 6.66 bits |
| Pixel Range | `range` | > 206 |
| Dark Pixel Ratio | `dpr` | < 0.198 |
| Saturated Pixel Ratio | `spr` | < 0.088 |
| Quality Score | `score` | > 1800.0 |

If the metrics packet reports a non-zero status, the firmware omits the JPEG entirely and the GUI skips the image-receive phase.

---

## CSV format

All readings are written to `data/sensor_readings.csv`.

| Column | Description |
|--------|-------------|
| `instance_id` | Shared ID for every reading from one "Request Data" click, e.g. `INST_20260610_143022` |
| `metric_id` | Per-reading ID, e.g. `GPS_20260610_143022` |
| `metric_name` | GUI metric name, e.g. `"GPS"`, `"UV Index"` |
| `value` | Scalar string or comma-separated vector (GPS, IMU, Tilt, Temp External) |
| `unit` | Unit string matching `METRIC_RANGES[name][3]` in data_store.py |
| `timestamp` | `YYYY-MM-DD HH:MM:SS` |

Old CSVs without an `instance_id` column are migrated automatically on first load.

---

## GUI features

### Sensor cards
- **Right panel** (6 cards): Camera 1, Camera 2, EMI, Turbidity, Salinity, Battery
- **Bottom strip** (7 cards): GPS, Temp External, Temp Internal (Static), Temp Internal (Dynamic), IMU, UV Index, Tilt
- Click any card to open its detail view in the centre panel
- Checkbox on each card controls whether that sensor is included in the next request
- **Check All / Uncheck All** buttons in the toolbar

### Centre panel
- **Graph view**: time-series matplotlib plot for the selected metric; time range switchable (30 min / 1 hr / 1 week / All)
- **Camera view**: most recent JPEG + image-quality metrics panel
- **GPS map**: live tkintermapview map showing up to 3 most recent fixes; oldest→newest coloured yellow→orange→red
- **Data Log**: two-tab view (By Instance / Flat Table) with metric and time-range filtering

### Toolbar buttons
| Button | Action |
|--------|--------|
| ► Request Data | Sends a BLE command for all checked sensors |
| Check All / Uncheck All | Bulk-toggle all sensor checkboxes |
| Clear CSV | Wipes `sensor_readings.csv` after confirmation |
| Data Log | Opens the inline Data Log view |
| Lookup ID | Searchable history window across all metrics |
| Connect | Scans for buoy and connects |

### Auto-refresh
Cards refresh from CSV every 2500 ms (`REFRESH_MS` in constants.py) when no request is pending. This keeps the display current even when data was loaded from a previous session.

---

## Notes

- The BLE transport is a development proxy for the **Iridium 9603N** satellite modem. The 20-byte fragment size and command framing were chosen to fit within the Iridium SBD 340-byte message limit. Migrating to satellite requires replacing the Bleak UART calls with Iridium AT command sequences; the payload parsing logic is unchanged.

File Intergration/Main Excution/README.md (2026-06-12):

# Hub and Main Execution Loop

# 1. About

This directory documents the **command dispatch layer** of the ArcticSense firmware, which links the transport layer (BLE / Iridium) to the sensor and camera subsystems.

The hub is the central coordination point on each board:

- The **Motherboard (MB) hub** (`hub.h` / `hub.cpp`) receives 5-byte commands from the ground-station GUI over USART1, decodes the sensor bitmask, collects data from MB-resident sensors via the sensor registry, forwards the bitmask to the **Daughterboard (DB)** over USART6, and transmits the assembled response back to the GUI in 20-byte fragments.
- The **Daughterboard (DB) hub** (`db_hub.h` / `db_hub.cpp`) mirrors the MB hub in structure. It receives forwarded commands from the MB over USART2, collects data from DB-resident sensors, and returns the payload directly to the MB.

Both hubs follow the same interrupt-safe pattern: a UART RX interrupt populates a volatile flag and bitmask, and the main loop polls and dispatches on each iteration.

---

# 2. Architecture

```
GUI (Python / bleak)
      │  5-byte command
      ▼
 [MB USART1] ── HM-10 BLE ──► MB hub
                                │
                    ┌───────────┴────────────┐
                    │                        │
             MB sensor registry       [MB USART6]
           (UV, GPS, Tilt, Battery,         │
            EMI, Temp, Humidity)      [DB USART2]
                    │                        │
                    │                  DB sensor registry
                    │           (Thermistors, Salinity, Turbidity
                    │                IMU, Temp, Humidity)
                    │                        │
                    └───────────┬────────────┘
                                │  assembled payload
                         MB USART1
                                │
                           GUI (response)
```

Camera captures (CAM1, CAM2) are handled exclusively by the MB hub. The DB hub has no camera path.

---

# 3. Tested Hardware

| Board | MCU |
|-------|-----|
| Motherboard (MB) | STM32F405RGT6 |
| Daughterboard (DB) | STM32F405RGT6 |

---

# 4. Development Environment

| Tool | Version |
|------|---------|
| IDE | STM32CubeIDE |
| Version | 2.0.0 |
| Build | 26820_20251114_1348 |
| Vendor | STMicroelectronics |
| MCU | STM32F405RGT6 |
| Firmware Library | STM32 HAL |

---

# 5. UART Assignments

## Motherboard

| UART | Pins | Baud | Role |
|------|------|------|------|
| USART1 | PA9 (TX), PA10 (RX) | 9600 | BLE link to GUI via HM-10 |
| USART6 | PC6 (TX), PC7 (RX) | 115200 | Inter-board link to DB |

## Daughterboard

| UART | Pins | Baud | Role |
|------|------|------|------|
| USART2 | PA2 (TX), PA3 (RX) | 115200 | Inter-board link to MB |

---

# 6. API

## Motherboard Hub (`hub.h`)

| Function | Description |
|----------|-------------|
| `void hub_begin(void)` | Arms USART1 for byte-by-byte interrupt reception. Must be called once after `MX_USART1_UART_Init()`. |
| `void hub_process(void)` | Dispatches any pending command. Call from the main loop; returns immediately if no command is ready. |
| `void hub_on_rx_byte(void)` | ISR hook invoked from `HAL_UART_RxCpltCallback()`. Not called directly by application code. |

## Daughterboard Hub (`db_hub.h`)

| Function | Description |
|----------|-------------|
| `void hub_begin(void)` | Arms USART2 for byte-by-byte interrupt reception. Must be called once after `MX_USART2_UART_Init()`. |
| `void hub_process(void)` | Dispatches any pending command. Call from the DB main loop. |
| `void hub_on_rx_byte(void)` | ISR hook invoked from `HAL_UART_RxCpltCallback()` on USART2. |

---

# 7. Internal State

Both hubs share the same volatile-flag / main-loop-snapshot pattern. These variables are not exposed in the public API.

| Variable | Scope | Description |
|----------|-------|-------------|
| `hub_cmd_ready` | `volatile uint8_t` | Set by ISR when a valid command frame is received |
| `hub_cmd_mask` | `volatile uint32_t` | 24-bit sensor bitmask decoded from the last valid command |
| `hub_ack_received` | `volatile uint8_t` | Set by ISR when a `0xFF` ACK byte arrives *(MB only)* |
| `hub_frame_buf[CMD_LEN]` | `uint8_t` | Accumulates incoming bytes until a complete 5-byte frame is assembled |
| `hub_resp_buf[128]` | `uint8_t` | Output buffer for the assembled sensor payload |

---

# 8. Macros

| Macro | Value | Description |
|-------|-------|-------------|
| `ACK_TIMEOUT_MS` | `2000` | Milliseconds the MB waits for a GUI ACK before retrying |
| `MAX_RETRIES` | `3` | Maximum retransmission attempts per response |
| `CAMERA1_BIT` | `1` | Bitmask bit position for Camera 1 |
| `CAMERA2_BIT` | `2` | Bitmask bit position for Camera 2 |

---

# 9. Code Flow

### MB Hub — Receive Path (ISR)

1. `HAL_UART_RxCpltCallback` fires on USART1; calls `hub_on_rx_byte()`.
2. A standalone `0xFF` byte is recognised as an ACK; `hub_ack_received` is set and the frame buffer is reset.
3. Any `0xAC` byte resets the frame buffer to allow re-synchronisation after line noise.
4. Bytes accumulate in `hub_frame_buf` until 5 bytes have arrived.
5. On a complete frame, the CRC (`hub_frame_buf[4]`) is verified against `calc_crc(hub_frame_buf, 4)`.
6. If valid, the 24-bit mask is stored in `hub_cmd_mask` and `hub_cmd_ready` is set.
7. `HAL_UART_Receive_IT` is re-armed for the next byte.

### MB Hub — Dispatch Path (Main Loop)

1. `hub_process()` checks `hub_cmd_ready`; returns immediately if clear.
2. Interrupts are briefly disabled to take a consistent snapshot of `hub_cmd_mask` and clear both flags.
3. **Camera path**: if `CAMERA1_BIT` or `CAMERA2_BIT` is set, `send_jpeg_image()` is called with retry/ACK logic. Sensor collection is skipped.
4. **Sensor path**: `build_sensor_payload(mask, hub_resp_buf)` fills MB sensor data. `db_forward(mask, out)` forwards the same mask to the DB over USART6 and appends the returned DB payload. The combined buffer is sent to the GUI with `send_with_retry()`.

### DB Hub — Receive and Dispatch Path

The DB hub mirrors the MB receive path, using USART2 instead of USART1. No ACK detection is needed (the DB is never the retry initiator). On a valid command:

1. `build_sensor_payload(mask, hub_resp_buf)` fills DB sensor data.
2. `send_fragments()` transmits the response directly to the MB over USART2.
3. The DB does not wait for ACK; the MB handles retries.

---

# 10. Main Execution Loop

Both boards follow the same startup and loop structure:

```c
int main(void)
{
    HAL_Init();
    SystemClock_Config();

    /* Peripheral initialisation (CubeMX-generated) */
    MX_GPIO_Init();
    MX_DMA_Init();
    MX_USART1_UART_Init();
    /* ... other peripherals ... */

    /* Application initialisation */
    sensors_init();   /* calls init() for every sensor in REGISTRY[] */
    hub_begin();      /* arms UART RX interrupt */

    while (1)
    {
        hub_process();  /* dispatch any pending command */
    }
}
```

`hub_process()` is the only call in the main loop. All sensor reads, inter-board forwarding, fragmentation, and retransmission occur inside that function on demand, triggered by the interrupt-set `hub_cmd_ready` flag.

**Important**: `sensors_init()` must be called after all `MX_*_Init()` functions. HAL-dependent drivers (I2C, SPI, ADC) initialise lazily via their `init()` callbacks, which require the HAL to be fully up.

---

# 11. Sensor Registry Integration

The hub does not know which sensors exist. It delegates sensor collection entirely to the registry API:

| Function | Header | Description |
|----------|--------|-------------|
| `void sensors_init(void)` | `sensor_registry.h` | Calls `init()` on every `Sensor` in `REGISTRY[]` |
| `uint16_t build_sensor_payload(uint32_t mask, uint8_t *buf)` | `sensor_registry.h` | Iterates `REGISTRY[]`; for each sensor whose `bit` is set in `mask`, calls `read()` and appends `size` bytes to `buf`. Returns bytes written. |

The `Sensor` struct and the `REGISTRY[]` array are the only integration points. Adding a new sensor requires no changes to the hub or the main loop.

### Bitmask Layout

| Bit | Board | Sensor |
|-----|-------|--------|
| 0 | MB | UV / ALS (LTR390) |
| 1 | MB | Camera 1 (OV2640) |
| 2 | MB | Camera 2 (OV2640) |
| 3 | MB | GPS |
| 4 | MB | Tilt (IIS2ICLX) |
| 5 | MB | Battery Monitor (INA219) |
| 6 | MB | EMI (lock-in) |
| 7 | MB | Humidity / Temperature (SHT45) |
| 11 | DB | Humidity / Temperature (SHT45) |
| 12 | DB | Thermistors ×4 (PS103J2) |
| 13 | DB | Turbidity |
| 14 | DB | IMU (MPU6050) |

---

# 12. Dependencies

- **STM32 HAL library**
- **UART peripherals**: USART1 (MB BLE link), USART6 (MB inter-board), USART2 (DB inter-board)
- `protocol.h` / `protocol.c` (MB) — fragmentation and CRC
- `db_protocol.h` / `db_protocol.c` (DB) — fragmentation and CRC
- `sensor_registry.h` / `sensor_registry.cpp` (MB) — sensor dispatch
- `db_sensor_registry.h` / `db_sensor_registry.cpp` (DB) — sensor dispatch
- `camera.h` (MB) — camera capture path

---

# 13. Notes

- **ISR / main-loop safety**: `hub_cmd_ready`, `hub_cmd_mask`, and `hub_ack_received` are `volatile` and are read with `__disable_irq()` / `__enable_irq()` to ensure a consistent snapshot. Never read these directly from application code.
- **Camera and sensor paths are mutually exclusive**: if any camera bit is set in the mask, sensor collection is skipped entirely in that command cycle. The GUI issues separate requests for camera and sensor data.
- **DB hub sends no ACK**: the DB relies on the MB to detect missing responses and re-issue the command. If the DB is silent (e.g. `len == 0`), the MB's `HAL_UART_Receive` will time out after 500 ms and `db_forward` will return 0.
- **CubeMX regeneration pitfall**: `main.cpp` is renamed from `main.c` to support C++. CubeMX does not update this file on regeneration. All calls to `sensors_init()` and `hub_begin()` must remain inside `USER CODE` blocks to survive a CubeMX regeneration.
- **`HAL_MAX_DELAY` must not be used** in UART polling calls inside the hub. All `HAL_UART_Receive` and `HAL_UART_Transmit` calls use finite timeouts (100–500 ms) to prevent the main loop from blocking indefinitely on a disconnected peripheral.
- **Iridium Migration**: the hub's reactive command-response model must be replaced with autonomous scheduled transmission. The polling loop becomes timer driven building the payload directly without waiting for an incoming command. Each session will send the full sensor payload and image metadata. Camera images will only be sent on Mobile Terminated requests.

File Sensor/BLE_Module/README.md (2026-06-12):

# BLE / HM-10 Transport Layer

# 1. About

This directory contains the **wire protocol** used to transmit sensor data and camera imagery between the **Motherboard (MB)** and the **host ground-station GUI**.

During development and field trials, a **HM-10 BLE module** provides the physical link. The HM-10 operates as a transparent UART-to-BLE bridge: the STM32 firmware writes bytes to USART1 and the module forwards them over Bluetooth Low Energy to the host PC, where the Python GUI receives them via the `bleak` library. No BLE-specific commands are issued by the firmware; from the STM32's perspective the link is a plain serial port.

The protocol is deliberately designed to match the **340-byte SBD message limit of the Iridium 9603N** satellite modem that will replace the HM-10 for polar deployment. Each command and each fragment fits within that constraint, so the firmware transport layer can be substituted at compile time without changing the application logic.

The protocol layer consists of two files:

- `protocol.h` / `protocol.c` — framing, CRC, and fragment transmission for the **MB → GUI** link (USART1)
- `db_protocol.h` / `db_protocol.c` — an identical framing layer for the **MB → DB** inter-board link (USART6/USART2); see [Section 11](#11-inter-board-link-differences) for differences

---

# 2. Part Information

The BLE module used is the **HM-10**, a BLE 4.0 module with a transparent UART interface.

| Property | Value |
|----------|-------|
| Interface | UART (transparent serial) |
| Baud rate | 9600 |
| BLE standard | Bluetooth 4.0 LE |
| Default role | Peripheral (connectable) |
| Default name | `HMSoft` |

The HM-10 requires no firmware-level BLE commands. It is configured once over AT commands at power-on and then acts as a wire.
---

# 3. Tested Hardware

This driver has been tested with:

- **STM32F405RGT6**
- **HM-10 BLE module**
- **Python GUI** 

---

# 4. Development Environment

| Tool | Version |
|------|---------|
| IDE | STM32CubeIDE |
| Version | 2.0.0 |
| Build | 26820_20251114_1348 |
| Vendor | STMicroelectronics |
| MCU | STM32F405RGT6 |
| Firmware Library | STM32 HAL |

---

# 5. Hardware Connections

The HM-10 communicates with the STM32 Motherboard over a **UART interface**.

## STM32 MB ↔ HM-10 Connections

| HM-10 Pin | STM32 Peripheral | Description |
|-----------|-----------------|-------------|
| VCC | 3.3V | Power supply |
| GND | GND | Ground |
| TX | USART1_RX (PA10) | HM-10 transmits to STM32 |
| RX | USART1_TX (PA9) | STM32 transmits to HM-10 |

## STM32 MB Pin Mapping

| STM32 Pin | Peripheral | Function |
|-----------|-----------|----------|
| PA9 | USART1_TX | Sends fragments and ACKs to GUI via HM-10 |
| PA10 | USART1_RX | Receives commands and ACKs from GUI via HM-10 |

**UART settings:** 9600 baud

---

# 6. API

The protocol layer exposes two functions, both declared in `protocol.h`:

| Header | Function | Description |
|--------|----------|-------------|
| `protocol.h` | `uint8_t calc_crc(const uint8_t *buf, uint8_t len)` | Checksum over `len` bytes of `buf`. Used to validate commands and authenticate fragments. |
| `protocol.h` | `void send_fragments(const uint8_t *buf, uint32_t len, uint8_t stx_more, uint8_t stx_last)` | Splits `buf` into 16-byte payload fragments and transmits each as a 20-byte packet over USART1. The last fragment uses `stx_last`; all others use `stx_more`. |

The application layer (`hub.cpp`) calls `send_fragments` directly. The protocol layer has no knowledge of sensors, cameras, or the hub state machine.

---

# 7. Frame Definitions

## Command Frame (GUI → MB)

Sent by the host to request data. 5 bytes total.

| Byte | Field | Value |
|------|-------|-------|
| 0 | STX | `0xAC` |
| 1 | `MASK_L` | Bits 0–7 of the 24-bit sensor bitmask |
| 2 | `MASK_M` | Bits 8–15 of the 24-bit sensor bitmask |
| 3 | `MASK_H` | Bits 16–23 of the 24-bit sensor bitmask |
| 4 | CRC | Checksum of bytes 0–3 |

## Sensor Fragment (MB → GUI)

Each response is split into one or more 20-byte fragments.

| Byte | Field | Description |
|------|-------|-------------|
| 0 | STX | `0xAA` (more to follow) or `0xAF` (last fragment) |
| 1 | IDX_H | High byte of fragment index |
| 2 | IDX_L | Low byte of fragment index |
| 3–18 | Payload | Up to 16 bytes of sensor data |
| 19 | CRC | Checksum of bytes 0–18 |

The last fragment is zero-padded if the total payload length is not a multiple of 16.

## Image Fragment (MB → GUI)

| Byte | Field | Description |
|------|-------|-------------|
| 0 | STX | `0xA0` (more bytes), `0xA1` (last bytes), `0xA2` (metadata more), `0xA3` (metadata last) |
| 1 | IDX_H | High byte of fragment index |
| 2 | IDX_L | Low byte of fragment index |
| 3–18 | Payload | 16 bytes of JPEG data or image quality metadata |
| 19 | CRC | XOR of bytes 0–18 |

## ACK Byte (GUI → MB)

A single byte `0xFF` sent by the GUI to acknowledge receipt of a complete response. The MB retries transmission up to `MAX_RETRIES` times if no ACK arrives within `ACK_TIMEOUT_MS`.

---

# 8. Macros

| Header | Macro | Value | Description |
|--------|-------|-------|-------------|
| `protocol.h` | `STX_SENSOR_MORE` | `0xAA` | Sensor fragment, more to follow |
| `protocol.h` | `STX_SENSOR_LAST` | `0xAF` | Sensor fragment, final |
| `protocol.h` | `STX_IMAGE_MORE` | `0xA0` | Image fragment, more to follow |
| `protocol.h` | `STX_IMAGE_LAST` | `0xA1` | Image fragment, final |
| `protocol.h` | `STX_IMAGE_META_MORE` | `0xA2` | Image quality metadata fragment, more to follow |
| `protocol.h` | `STX_IMAGE_META_LAST` | `0xA3` | Image quality metadata fragment, final |
| `protocol.h` | `STX_CMD` | `0xAC` | Start-of-command byte |
| `protocol.h` | `STX_ACK` | `0xFF` | ACK byte |
| `protocol.h` | `CMD_LEN` | `5` | Command frame length in bytes |
| `protocol.h` | `FRAG_SIZE` | `20` | Fragment frame length in bytes |
| `protocol.h` | `PAYLOAD_BYTES` | `16` | Payload bytes per fragment |

---

# 9. Code Flow

### Outbound (MB → GUI)

1. Hub builds the sensor or image payload in a local buffer.
2. `send_fragments()` divides the buffer into 16-byte chunks.
3. Each chunk is wrapped in a 20-byte frame: `[STX][IDX_H][IDX_L][16 bytes payload][CRC]`.
4. Frames are transmitted over USART1 with a 20 ms inter-frame delay to allow the HM-10 BLE module time between packets.
5. After all fragments are sent, the MB waits up to `ACK_TIMEOUT_MS` (2000 ms) for a `0xFF` ACK from the GUI. Up to `MAX_RETRIES` (3) retransmission attempts are made.

### Inbound (GUI → MB)

1. USART1 is armed for byte-by-byte interrupt reception via `HAL_UART_Receive_IT`.
2. Each byte is appended to a 5-byte frame buffer.
3. On a complete frame, the CRC is verified. A valid frame sets the `hub_cmd_ready` flag and stores the decoded 24-bit bitmask.
4. A standalone `0xFF` byte is recognised as an ACK and sets `hub_ack_received` without disturbing the command framing state.

---

# 10. Host Interface

The host-side counterpart is `ble_manager.py` in the Python ground-station GUI. It uses the `bleak` library to connect to the HM-10's BLE GATT characteristic and exchanges bytes using the same frame format defined in this document.

From the host's perspective:

- **Sending a command**: write a 5-byte command frame to the GATT TX characteristic.
- **Receiving a response**: collect 20-byte notification frames until a `STX_SENSOR_LAST` or `STX_IMAGE_LAST` STX byte is received. Send `0xFF` to the TX characteristic to ACK.
- **Sensor payload layout**: bytes arrive in the order that sensors appear in `REGISTRY[]` in `sensor_registry.cpp`. The host must know the `size` of each requested sensor to parse the concatenated payload.

See `ble_manager.py` for the complete host-side implementation.

---

# 11. Inter-Board Link Differences

The `db_protocol.h` / `db_protocol.c` files implement the same CRC and fragmentation logic for the **MB ↔ DB UART link** (USART6 on the MB, USART2 on the DB). Two differences apply:

1. **UART handle**: `db_protocol.c` transmits on `huart2` (DB inter-board link) rather than `huart1` (BLE to GUI).
2. **Last-fragment IDX_L encoding**: On the DB link, the `IDX_L` byte of the final fragment is repurposed to carry the number of valid payload bytes in that fragment. The MB's `db_forward()` reads `frag[2]` as the byte count on the last fragment. This eliminates the need for the MB to maintain a sensor-size lookup table for DB sensors.
3. **No inter-frame delay**: The 20 ms `HAL_Delay` present in `protocol.c` is omitted from `db_protocol.c`. The direct UART connection between boards does not require the pacing that the HM-10 BLE module needs.

---

# 12. Dependencies

- **STM32 HAL library**
- **UART peripheral** (USART1 at 9600 baud for the BLE link)

---

# 13. Example Usage

```c
#include "protocol.h"

/* Transmit a 20-byte sensor payload as fragments */
uint8_t payload[20] = { /* sensor bytes */ };
send_fragments(payload, sizeof(payload), STX_SENSOR_MORE, STX_SENSOR_LAST);

/* Compute and verify a CRC */
uint8_t frame[5] = { 0xAC, 0x01, 0x00, 0x00, 0x00 };
frame[4] = calc_crc(frame, 4);
```

---

# 14. Notes

- The 9600 baud rate is dictated by the HM-10's default UART configuration. Higher baud rates are possible by AT command but have not been tested.
- The 20 ms inter-frame delay in `protocol.c` is required to prevent the HM-10 BLE module from dropping bytes at 9600 baud. Remove or reduce this delay only after testing throughput at the target rate.
- Each 20-byte fragment fits within the Iridium 9603N SBD 340-byte message limit. The BLE → Iridium transport substitution therefore requires changes only to the physical layer (`huart1` handle and baud rate), not to the framing logic.
- Camera JPEG data is too large for reliable Iridium SBD transmission. Further tests are needed to verify the image transmission. Scalar sensor data and image quality metadata are suitable for satellite uplink.

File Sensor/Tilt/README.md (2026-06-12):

# Tilt Sensor Driver — IIS2ICLX (STM32)

# 1. About

This directory contains the driver for the **IIS2ICLX** dual-axis digital inclinometer used to monitor tilt.

Accurate tilt measurement is important for two reasons. First, it allows the ground station to detect whether the buoy has capsized or been displaced from a stable vertical orientation, which would affect the validity of other sensor readings. Second, tilt data can be used to compensate directional sensors (e.g. the EMI coil orientation) for angular offsets.

The driver:

- Configures the IIS2ICLX over SPI for the correct full-scale range and output data rate
- Reads raw X and Y axis acceleration values
- Applies an **exponential moving average (EMA)** filter to reduce noise
- Converts filtered acceleration values to **roll and pitch angles** in degrees

---

# 2. Part Information

| Field | Value |
|-------|-------|
| Manufacturer | STMicroelectronics |
| Part Number | IIS2ICLX |
| Type | 2-axis digital inclinometer |
| Full-scale range | ±0.5 g (CTRL1_XL = 0x1C) |
| Sensitivity | 0.061 mg/LSB |
| Interface | SPI |

**Datasheet:** https://www.st.com/en/mems-and-sensors/iis2iclx.html

> **Note:** The `FS_XL[1:0]` field in CTRL1_XL uses a non-standard encoding for the IIS2ICLX. A value of `0b11` selects **±0.5 g** at 0.061 mg/LSB, which is the opposite of the standard accelerometer convention. Do not change `CTRL1_XL` from `0x1C` without consulting the IIS2ICLX datasheet.

---

# 3. Tested Hardware

This driver has been tested with:

- **STM32F405RGT6** 
- **IIS2ICLX** 

---

# 4. Development Environment

| Tool | Version |
|------|---------|
| IDE | STM32CubeIDE |
| Version | 2.0.0 |
| Build | 26820_20251114_1348 |
| Vendor | STMicroelectronics |
| MCU | STM32F405RGT6 |
| Firmware Library | STM32 HAL |

---

# 5. Hardware Connections

The IIS2ICLX communicates with the STM32 over a 4-wire SPI interface.

## STM32 ↔ IIS2ICLX Connections

| IIS2ICLX Pin | STM32 Peripheral | Description |
|-------------|-----------------|-------------|
| VDD / VDDIO | 3.3 V | Power supply |
| GND | GND | Ground |
| SCL | SPI_SCK | SPI clock |
| SDA | SPI_MOSI | SPI data in |
| SDO | SPI_MISO | SPI data out |
| CS | GPIO Output | SPI chip select (active low) |

> **Note:** The SPI clock prescaler must be set to keep SCK within the IIS2ICLX maximum operating frequency.

---

# 6. API

## Functions

| Header | Function | Description |
|--------|----------|-------------|
| `tilt.h` | `void tilt_init(const Tilt_HandleTypeDef *tilt)` | Configures the IIS2ICLX over SPI and starts the EMA timer |
| `tilt.h` | `Tilt_Status tilt_read(const Tilt_HandleTypeDef *tilt, Tilt_DataTypeDef *data)` | Reads the latest EMA-filtered tilt angles |
| `tilt.h` | `void tilt_ema_update(void)` | Updates the EMA filter with a fresh ADC reading — called from the hardware timer ISR |

---

# 7. Data Types (Structs)

## Tilt_HandleTypeDef

| Type | Field | Description |
|------|-------|-------------|
| `SPI_HandleTypeDef *` | `spi` | SPI handle connected to the IIS2ICLX |
| `GPIO_TypeDef *` | `cs_port` | GPIO port for the SPI chip select pin |
| `uint16_t` | `cs_pin` | GPIO pin for the SPI chip select |
| `TIM_HandleTypeDef *` | `tim` | Timer handle used to periodically drive the EMA filter |

## Tilt_DataTypeDef

When `tilt.h` is included, a **global instance** of `Tilt_DataTypeDef` called `TILT` is created. The driver populates this structure after each call to `tilt_read()`.

| Type | Field | Description |
|------|-------|-------------|
| `Tilt_Status` | `status` | Indicates whether the read succeeded |
| `int16_t` | `raw_x` | Raw X-axis output register value |
| `int16_t` | `raw_y` | Raw Y-axis output register value |
| `float` | `ema_x` | EMA-filtered X-axis acceleration (g) |
| `float` | `ema_y` | EMA-filtered Y-axis acceleration (g) |
| `float` | `roll_deg` | Roll angle in degrees, derived from ema_x and ema_y |
| `float` | `pitch_deg` | Pitch angle in degrees, derived from ema_x and ema_y |

---

# 8. Macros

| Header | Macro | Description |
|--------|-------|-------------|
| `tilt.h` | `TILT_EMA_ALPHA` | EMA smoothing factor (0 < α ≤ 1); lower values give more smoothing |
| `tilt.h` | `TILT_SENSITIVITY` | Sensor sensitivity in g/LSB (0.061e-3 for CTRL1_XL = 0x1C) |
| `tilt.h` | `TILT_TIMER_PERIOD_MS` | EMA update interval in milliseconds (~80 ms) |

---

# 9. Enums
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

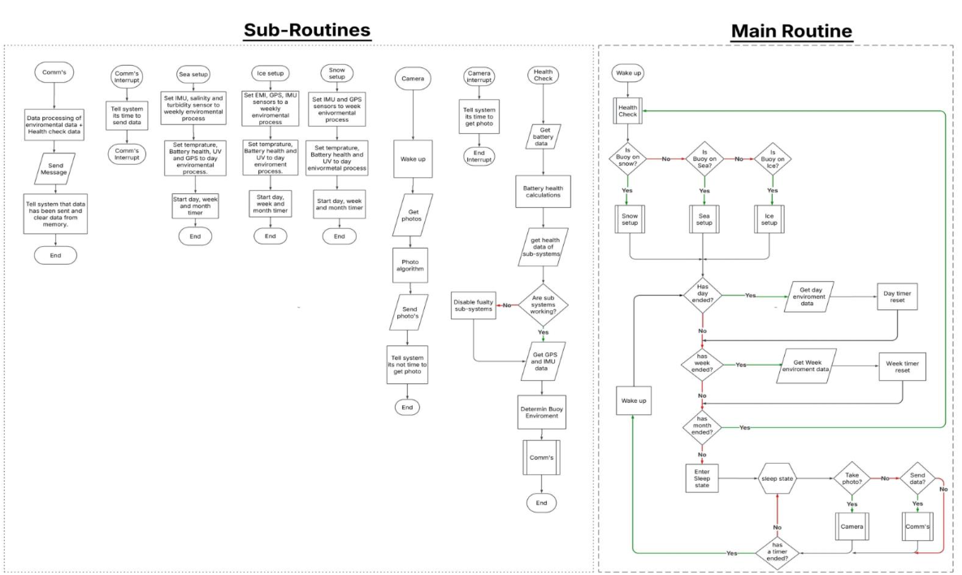
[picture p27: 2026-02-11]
Sensor/images/Software Architecture.png

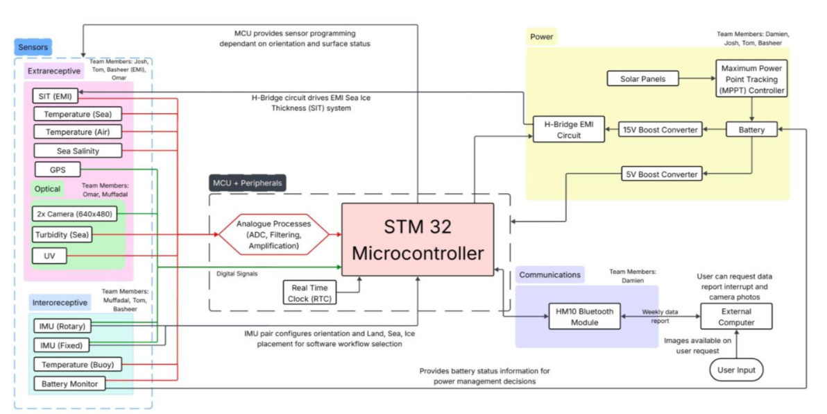
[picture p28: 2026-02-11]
Sensor/images/Hardware Artitecture.png

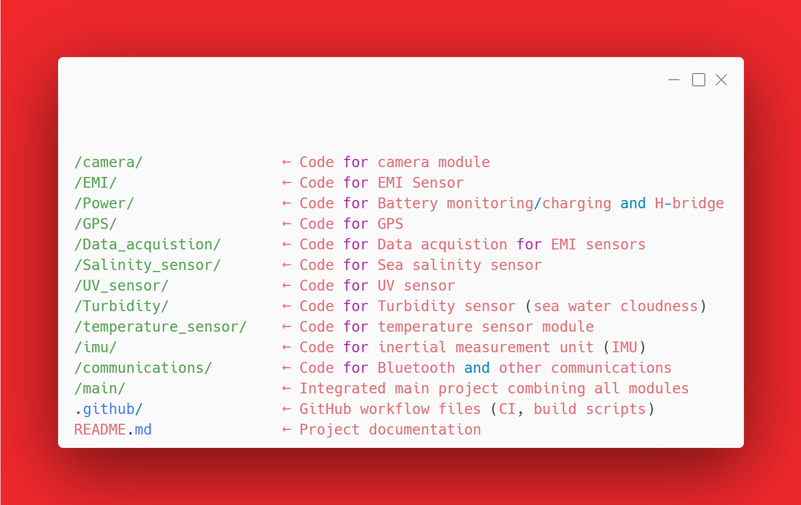
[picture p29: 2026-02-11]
Sensor/images/FilePathFigure.png

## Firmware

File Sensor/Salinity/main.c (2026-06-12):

/* USER CODE BEGIN Header */
/**
  ******************************************************************************
  * @file           : main.c
  * @brief          : Main program body — Conductivity / Salinity Measurement
  ******************************************************************************
  * @attention
  *
  * Copyright (c) 2026 STMicroelectronics.
  * All rights reserved.
  *
  * This software is licensed under terms that can be found in the LICENSE file
  * in the root directory of this software component.
  * If no LICENSE file comes with this software, it is provided AS-IS.
  *
  ******************************************************************************
  */
/* USER CODE END Header */

/* Includes ------------------------------------------------------------------*/
#include "main.h"
#include "adc.h"
#include "dac.h"
#include "dma.h"
#include "i2c.h"
#include "tim.h"
#include "usart.h"
#include "gpio.h"

/* USER CODE BEGIN Includes */
#include <math.h>
#include <string.h>
#include <stdio.h>
/* USER CODE END Includes */

/* Private typedef -----------------------------------------------------------*/
/* USER CODE BEGIN PTD */

typedef enum {
    COND_OK = 0,
    COND_FAULT_SHORT,       /* ADC read ~3.3 V before excitation — short/fault */
    COND_FAULT_TIMEOUT      /* DMA never completed                              */
} ConductivityStatus;

typedef struct {
    ConductivityStatus  status;
    float               adc1_rms_V;       /* Current channel RMS voltage (V)  */
    float               adc2_rms_V;       /* Voltage channel RMS voltage (V)  */
    float               conductivity_mS;
    float               salinity_gL;
} ConductivityResult;

/* USER CODE END PTD */

/* Private define ------------------------------------------------------------*/
/* USER CODE BEGIN PD */

/* --- Sine / DAC ---------------------------------------------------------- */
#define SINE_SAMPLES        64            /* LUT points per cycle             */
#define SINE_FREQ_HZ        7.0f          /* excitation frequency (Hz)        */

/* DAC 1 Vpp centred at mid-rail 1.65 V  (VDDA = 3.3 V, 12-bit)
   mid = 4095 * 0.5        = 2047
   amp = 4095 * (0.5/3.3)  = 620   -> +/-0.5 V = 1 Vpp                     */
#define DAC_MID_COUNT       2047
#define DAC_AMP_COUNT       620

/* --- ADC capture --------------------------------------------------------- */
/* 16 complete cycles -> 16 * 64 = 1024 dual-word samples                   */
#define CYCLES_TO_CAPTURE   16
#define ADC_BUF_SIZE        (CYCLES_TO_CAPTURE * SINE_SAMPLES)  /* 1024     */

#define VREF                3.3f
#define ADC_FULL_SCALE      4095.0f

/* Safety: if either ADC reads this or above (~3.22 V) before the DAC
   starts, the probe is shorted — abort everything immediately               */
#define ADC_SAFETY_THRESHOLD  4000u

/* --- Conversion constants ------------------------------------------------ */
#define CONDUCTIVITY_SCALE  14.02f    /* (I_rms / V_rms) -> conductivity mS  */
#define SALINITY_SCALE      24.46f    /* conductivity mS -> salinity g/L     */

/* USER CODE END PD */

/* Private macro -------------------------------------------------------------*/
/* USER CODE BEGIN PM */
/* USER CODE END PM */

/* Private variables ---------------------------------------------------------*/

/* USER CODE BEGIN PV */
static uint16_t          sine_lut[SINE_SAMPLES];
static uint32_t          adc_buf[ADC_BUF_SIZE]; /* packed [ADC2(31:16)|ADC1(15:0)] */
static volatile uint8_t  adc_dma_done = 0;
/* USER CODE END PV */

/* Private function prototypes -----------------------------------------------*/
void SystemClock_Config(void);

/* USER CODE BEGIN PFP */
static void               BuildSineLUT(void);
static ConductivityStatus SafetyCheck(void);
static float              ComputeRMS(const uint32_t *buf, uint32_t len, uint8_t shift);
ConductivityResult        Conductivity_Measure(void);
/* USER CODE END PFP */

/* ============================================================================
   USER CODE BEGIN 0
   ============================================================================ */

/**
  * @brief  Build a 64-point sine LUT scaled for 1 Vpp centred at mid-rail.
  */
static void BuildSineLUT(void)
{
    for (int i = 0; i < SINE_SAMPLES; i++) {
        float angle = 2.0f * (float)M_PI * i / SINE_SAMPLES;
        sine_lut[i] = (uint16_t)(DAC_MID_COUNT
                      + (int32_t)(DAC_AMP_COUNT * sinf(angle)));
    }
}

/**
  * @brief  Safety check — one poll-mode conversion BEFORE the DAC starts.
  *         If either ADC input is already near 3.3 V the circuit is faulty.
  *
  *         After the poll-mode conversion the ADCs are re-initialised so they
  *         are back in the timer-triggered DMA state CubeMX configured.
  *
  * @retval COND_OK, COND_FAULT_SHORT, or COND_FAULT_TIMEOUT
  */
static ConductivityStatus SafetyCheck(void)
{
    HAL_ADC_Start(&hadc2);
    HAL_ADC_Start(&hadc1);

    if (HAL_ADC_PollForConversion(&hadc1, 10) != HAL_OK) {
        HAL_ADC_Stop(&hadc1);
        HAL_ADC_Stop(&hadc2);
        return COND_FAULT_TIMEOUT;
    }

    uint32_t raw1 = HAL_ADC_GetValue(&hadc1);
    uint32_t raw2 = HAL_ADC_GetValue(&hadc2);

    HAL_ADC_Stop(&hadc1);
    HAL_ADC_Stop(&hadc2);

    /* Restore ADCs to DMA-triggered state */
    MX_ADC1_Init();
    MX_ADC2_Init();

    if (raw1 >= ADC_SAFETY_THRESHOLD || raw2 >= ADC_SAFETY_THRESHOLD) {
        return COND_FAULT_SHORT;
    }

    return COND_OK;
}

/**
  * @brief  Compute AC-RMS of one channel from the interleaved dual-ADC buffer.
  *
  *         Dual-simultaneous DMA packs each word as:
  *           bits [15: 0] = ADC1 result  (shift =  0)
  *           bits [31:16] = ADC2 result  (shift = 16)
  *
  *         DC is removed by subtracting the mean first so the mid-rail DAC
  *         bias does not inflate the RMS result.
  *
  * @param  buf    Pointer to 32-bit dual-word buffer
  * @param  len    Number of 32-bit entries
  * @param  shift  0 for ADC1, 16 for ADC2
  * @retval AC RMS voltage in volts
  */
static float ComputeRMS(const uint32_t *buf, uint32_t len, uint8_t shift)
{
    /* Pass 1 — mean (DC component) */
    double sum = 0.0;
    for (uint32_t i = 0; i < len; i++) {
        uint16_t raw = (uint16_t)((buf[i] >> shift) & 0x0FFFu);
        sum += (double)raw;
    }
    double mean = sum / (double)len;

    /* Pass 2 — variance then RMS (AC only) */
    double sq_sum = 0.0;
    for (uint32_t i = 0; i < len; i++) {
        uint16_t raw = (uint16_t)((buf[i] >> shift) & 0x0FFFu);
        double ac = (double)raw - mean;
        sq_sum += ac * ac;
    }

    double rms_counts = sqrt(sq_sum / (double)len);
    return (float)(rms_counts * VREF / ADC_FULL_SCALE);
}

/**
  * @brief  DMA transfer-complete callback (overrides HAL weak implementation).
  *         Sets the flag that unblocks Conductivity_Measure().
  */
void HAL_ADC_ConvCpltCallback(ADC_HandleTypeDef *hadc)
{
    if (hadc->Instance == ADC1) {
        adc_dma_done = 1;
    }
}

/**
  * @brief  Run one full conductivity / salinity measurement.
  *
  *         Steps:
  *           1. Safety check  — abort if ADC reads ~3.3 V with no excitation
  *           2. Start DAC sine wave + TIM6
  *           3. 50 ms settle
  *           4. Capture 1024 dual samples via DMA (TIM3 triggered)
  *           5. Stop all peripherals cleanly
  *           6. Compute RMS, conductivity, salinity
  *
  * @retval ConductivityResult  — always check .status before using values
  */
ConductivityResult Conductivity_Measure(void)
{
    ConductivityResult result;
    memset(&result, 0, sizeof(result));

    /* Step 1 — safety pre-check (no excitation yet) ----------------------- */
    result.status = SafetyCheck();
    if (result.status != COND_OK) {
        return result;
    }

    /* Step 2 — build LUT, start DAC + TIM6 -------------------------------- */
    BuildSineLUT();

    HAL_DAC_Start_DMA(&hdac,
                      DAC_CHANNEL_2,
                      (uint32_t *)sine_lut,
                      SINE_SAMPLES,
                      DAC_ALIGN_12B_R);

    HAL_TIM_Base_Start(&htim6);   /* triggers DAC at 64*7 = 448 Hz          */

    /* Step 3 — settle ------------------------------------------------------ */
    HAL_Delay(50);                /* ~half a 7 Hz cycle                      */

    /* Step 4 — start ADC DMA capture --------------------------------------- */
    adc_dma_done = 0;
    memset(adc_buf, 0, sizeof(adc_buf));

    HAL_ADC_Start(&hadc2);                              /* slave first        */
    HAL_ADC_Start_DMA(&hadc1, adc_buf, ADC_BUF_SIZE);  /* master + DMA       */
    HAL_TIM_Base_Start(&htim3);                         /* start ADC trigger  */

    /* Wait for DMA complete (3 s timeout) ---------------------------------- */
    uint32_t t_start = HAL_GetTick();
    while (!adc_dma_done) {
        if ((HAL_GetTick() - t_start) > 3000u) {
            result.status = COND_FAULT_TIMEOUT;
            goto cleanup;
        }
    }

    /* Step 5 — stop peripherals ------------------------------------------- */
    HAL_TIM_Base_Stop(&htim3);
    HAL_ADC_Stop_DMA(&hadc1);
    HAL_ADC_Stop(&hadc2);

    HAL_TIM_Base_Stop(&htim6);
    HAL_DAC_Stop_DMA(&hdac, DAC_CHANNEL_2);

    /* Park PA5 at mid-rail then stop — prevents floating output glitch     */
    HAL_DAC_SetValue(&hdac, DAC_CHANNEL_2, DAC_ALIGN_12B_R, DAC_MID_COUNT);
    HAL_DAC_Start(&hdac, DAC_CHANNEL_2);
    HAL_Delay(1);
    HAL_DAC_Stop(&hdac, DAC_CHANNEL_2);

    /* Step 6 — compute results -------------------------------------------- */
    float rms_I = ComputeRMS(adc_buf, ADC_BUF_SIZE, 0);   /* ADC1 IN9  — I  */
    float rms_V = ComputeRMS(adc_buf, ADC_BUF_SIZE, 16);  /* ADC2 IN14 — V  */

    result.adc1_rms_V = rms_I;
    result.adc2_rms_V = rms_V;

    if (rms_V < 1e-6f) {
        /* V channel is essentially zero — likely open circuit              */
        result.status = COND_FAULT_SHORT;
        return result;
    }

    result.conductivity_mS = (rms_I / rms_V) * CONDUCTIVITY_SCALE;
    result.salinity_gL     = result.conductivity_mS * SALINITY_SCALE;
    result.status          = COND_OK;
    return result;

cleanup:
    /* Emergency stop — shut everything down in the correct order           */
    HAL_TIM_Base_Stop(&htim3);
    HAL_TIM_Base_Stop(&htim6);
    HAL_ADC_Stop_DMA(&hadc1);
    HAL_ADC_Stop(&hadc2);
    HAL_DAC_Stop_DMA(&hdac, DAC_CHANNEL_2);
    HAL_DAC_Stop(&hdac, DAC_CHANNEL_2);
    return result;
}

/* USER CODE END 0 */
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

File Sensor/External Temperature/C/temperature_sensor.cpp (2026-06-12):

/*
 * temperature_sensor.cpp — DB thermistor driver
 *
 * All four channels use a single ADC1 peripheral with dynamic channel
 * switching. temp_sensor_init() overrides the CubeMX 4-channel scan
 * config to single-conversion mode; read_channel() then reconfigures
 * the channel register before each measurement.
 */

#include "temperature_sensor.h"
#include "main.h"
#include <math.h>
#include <string.h>

/* ── Steinhart–Hart beta equation constants (PS103J2 thermistor) ── */
#define REFERENCE_TEMP_K        298.15f    /* 25 °C in Kelvin          */
#define REFERENCE_RESISTANCE    10000.0f   /* 10 kΩ nominal at 25 °C   */
#define BETA_COEFFICIENT        3892.0f
#define ADC_MAX_COUNTS          4095.0f
#define ADC_REF_VOLTAGE         3.29f      /* VREF+ rail               */
#define FIXED_DIVIDER_RESISTOR  15000.0f   /* pull-up resistor         */
#define KELVIN_OFFSET           273.15f
#define N_SAMPLES               16         /* averaging window         */
#define ADC_TIMEOUT_MS          50

/* PC0–PC3 → ADC1_IN10–IN13 */
static const uint32_t CHANNELS[4] = {
    ADC_CHANNEL_10,
    ADC_CHANNEL_11,
    ADC_CHANNEL_12,
    ADC_CHANNEL_13,
};

/* ── Beta equation: voltage → °C ── */
static float voltage_to_temp(float v)
{
    if (v < 0.001f) return TEMPERATURE_ERROR_SENTINEL;  /* open-circuit */

    float R   = (ADC_REF_VOLTAGE * FIXED_DIVIDER_RESISTOR) / v
                 - FIXED_DIVIDER_RESISTOR;
    float inv = (1.0f / REFERENCE_TEMP_K)
                + (1.0f / BETA_COEFFICIENT) * logf(R / REFERENCE_RESISTANCE);
    return (1.0f / inv) - KELVIN_OFFSET;
}

/* ── Single-channel read: 1 dummy + N_SAMPLES averaged ── */
static float read_channel(uint8_t ch)
{
    HAL_ADC_Stop(&hadc1);

    ADC_ChannelConfTypeDef cfg = {0};
    cfg.Channel      = CHANNELS[ch];
    cfg.Rank         = 1;                    /* always rank 1: one channel at a time */
    cfg.SamplingTime = ADC_SAMPLETIME_480CYCLES;

    if (HAL_ADC_ConfigChannel(&hadc1, &cfg) != HAL_OK)
        return TEMPERATURE_ERROR_SENTINEL;

    /* Dummy conversion — settles ADC input capacitor after mux switch */
    HAL_ADC_Start(&hadc1);
    HAL_ADC_PollForConversion(&hadc1, ADC_TIMEOUT_MS);
    (void)HAL_ADC_GetValue(&hadc1);
    HAL_ADC_Stop(&hadc1);

    /* Averaged measurement */
    uint32_t sum = 0;
    for (int i = 0; i < N_SAMPLES; i++) {
        HAL_ADC_Start(&hadc1);
        if (HAL_ADC_PollForConversion(&hadc1, ADC_TIMEOUT_MS) != HAL_OK) {
            HAL_ADC_Stop(&hadc1);
            return TEMPERATURE_ERROR_SENTINEL;
        }
        sum += HAL_ADC_GetValue(&hadc1);
        HAL_ADC_Stop(&hadc1);
    }

    float raw  = (float)sum / (float)N_SAMPLES;
    float volt = (raw / ADC_MAX_COUNTS) * ADC_REF_VOLTAGE;
    return voltage_to_temp(volt);
}

/* ── Public API ── */

void temp_sensor_init(void)
{
    /*
     * CubeMX generates MX_ADC1_Init() with ScanConvMode=ENABLE and
     * NbrOfConversion=4 when four channels are configured with ranks 1–4.
     * read_channel() uses dynamic single-channel switching (rank always 1),
     * which conflicts with a 4-rank scan sequence.
     *
     * Override here to single-conversion mode so each HAL_ADC_Start()
     * converts exactly the one channel configured by the preceding
     * HAL_ADC_ConfigChannel() call.
     */
    HAL_ADC_Stop(&hadc1);
    hadc1.Init.ScanConvMode    = DISABLE;
    hadc1.Init.NbrOfConversion = 1;
    hadc1.Init.EOCSelection    = ADC_EOC_SINGLE_CONV;
    HAL_ADC_Init(&hadc1);
}

void temp_sensor_read(uint8_t *out, uint8_t *len_out)
{
    for (uint8_t ch = 0; ch < 4; ch++) {
        float t = read_channel(ch);
        memcpy(out + (ch * sizeof(float)), &t, sizeof(float));
    }
    if (len_out) *len_out = 16;
}

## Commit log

2025-11-26 Update README.md
    added in a Software Architecture section with an extra Figure of a flow chart
2026-02-11 This is the GPS code for the Adafruit ultimate, in this push the code has a function where it turns on or off gps module by the EN pin. additionally this has a function where it unitalizes the UART a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
2026-02-11 adding gps code, it contains a fuction to turn on and off by en pin. it has a fuction that reads uart and puts it in buffer, main int code as code that paraphase the buffer and has a fucntion where i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
2026-02-12 GPS Flow Diagram
    this shows how the code/function work in the GPS
2026-02-15 added a camera folder that contains code for the arducam. I think it works , i just need away of acessing the massive buffer that i get from it.
2026-02-17 new camera code that properly riggers the CS and uploades the camera settings to OV2640. in the ov2640 reg.h and .c has new struts fro resetting the sensor. there is also a lot of new functions that 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
2026-03-01 put camera C code into libries and change the layout of the Camera directories. added in an example. just need to update the readme and create a C++ version
2026-03-09 Code works and tested. everything is the code works. heres new: trueLengthFunction is now robust. the jpeg_decode actually works as intended. added new error messages to upload settings. also made th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
2026-03-10 upload camera flow diagram
2026-03-12 added in a new directory that has the waveshare lcd code, currently its in a main.c but will convert it to a .h and a.c and later to c++. also uploading an image to uses in the README
2026-03-16 uploaded LCD flow diagram
2026-04-02 added batteryMonitor code made by Basheer, with readme and example
2026-04-02 BatteryMonitor IC photo
2026-04-04 added block digram of battery monitor pipeline
2026-06-12 Adding in Sensors
2026-06-12 Update and rename db_sensor_registry.cpp to temperature_sensor.cpp
2026-06-12 Reorganize file structure and add new files
    [Duaghter_MCU.PrjPcb, Duaghter_STM.SchDoc, EMI Board.PrjPcb, EMI Schematic.SchDoc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]
2026-06-12 Remove PCB folder from repo, add to gitignore
    [Duaghter_MCU.PrjPcb, Duaghter_STM.SchDoc, EMI Board.PrjPcb, EMI Schematic.SchDoc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]
